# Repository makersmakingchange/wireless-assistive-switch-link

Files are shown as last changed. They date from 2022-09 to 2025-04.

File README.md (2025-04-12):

# Wireless Assistive Switch Link
The Wireless Assistive Switch Link is a device that enables a wireless connection between an assistive switch and an output device that has a 3.5 mm jack. In addition to momentary control, the device also has the option of pre-set timed latches of 10 seconds, 1 minute, or 5 minutes. This device may be useful for someone who would benefit from a wireless connection between the switch and the output device or using the latching feature for output devices. 

## Usage
An assistive switch is connected to the 3.5 mm jack on the transmitter. The 3.5 mm plug on the receiver is then connected to the input of the device to be controlled. With the receiver powered on, the receiver will activate the output device when the assistive switch is activated. 
The device can operate in several modes:

•	Momentary Switch: The output device will turn off about 0.5 seconds after the user stops pressing the switch.

•	Toggle Switch: Activating the assistive switch will activate the output device. The output device will remain on until the assistive switch is released, and pressed again. 

•	10 Second Latched Timer: After the assistive switch is pressed and released, the output device will remain on for 10 seconds and then turn off.

•	1 Minute Latched Timer: After the assistive switch is pressed and released, the output device will remain on for 1 minute and then turn off.

•	5 Minute Latched Timer: After the assistive switch is pressed and released, the output device will remain on for 5 minutes and then turn off. 

The mode can be changed by pressing the Mode Button on the Receiver. See the User Guide for instructions.

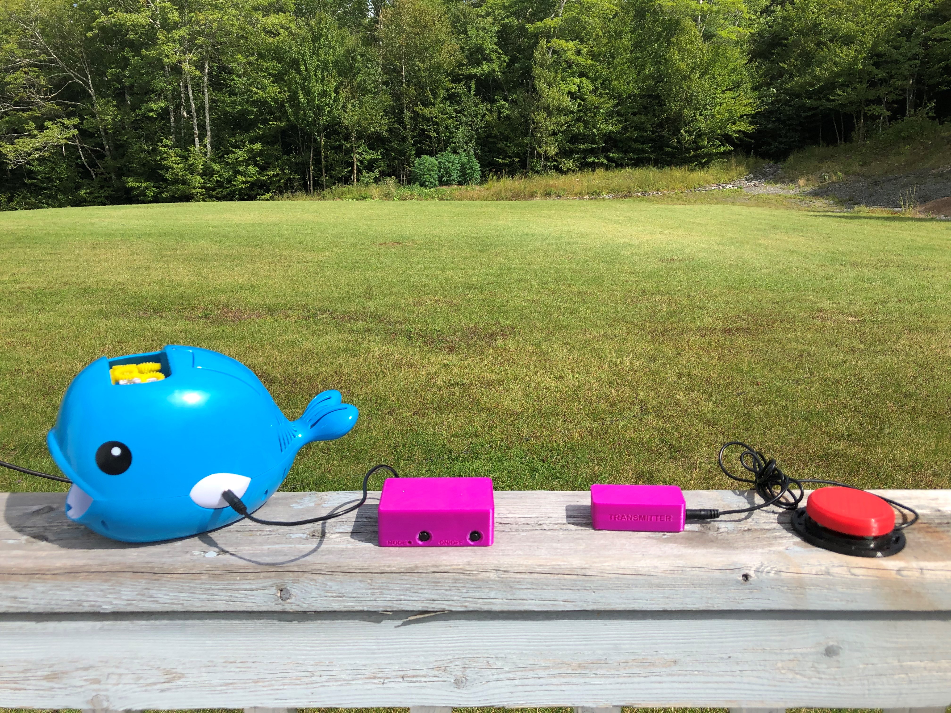
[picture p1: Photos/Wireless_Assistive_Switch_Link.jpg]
A picture of a 3d printed Wireless Assistive Switch Link. An Interact Switch is attached to the transmitter and a switch adapted whale toy is attached to the receiver.


## More info at
- [Makers Making Change Project Page](https://makersmakingchange.com/project/wireless-assistive-switch-link/)

## How to Obtain a Wireless Assistive Switch Link

### 1. Do it Yourself (DIY) or Do it Together (DIT)

This is an open-source assistive technology, so anyone is free to build it. All of the files and instructions required to build the device are contained within this repository. Refer to the Maker Checklist below.

### 2. Request a build of this device

If you would like to obtain this device, you may submit a build request through the [MMC Library Page](https://makersmakingchange.com/project/wireless-assistive-switch-link/). The requestor is responsible for the cost of materials and any shipping.

### 3. How to build this device for someone else

If you have the skills and equipment to build this device, and would like to donate your time to create the switch for someone who needs it, visit the [MMC Maker Wanted](https://makersmakingchange.com/maker-wanted/) section.

## Getting Started

### 1. Read the Makers Checklist

The Makers Checklist provides an overview of the steps required to build this device.

### 2. Order the Off-The-Shelf Components

The [Bill of Materials](/Documentation/Wireless_Assistive_Switch_Link_BOM_v1.0.xlsx) lists all of the parts and components required to build the Open Wobble Switch. The main switch component needs to be ordered online. The rest of the off-the-shelf components are also online or may be available in smaller quantities at your local hardware store or dollar store.

### 3. Print the 3D Printable components

All of the files and individual print files can be in the [/Build_Files/3D_Printing_Files](/Build_Files/3D_Printing/) folder.

### 4. Assemble the Device

Reference the [Assembly Guide](/Documentation/Wireless_Assistive_Switch_Link_Assembly_Guide_v1.0.pdf) for the tools and steps required to build each portion.

## Files
### Documentation
| Document             | Version | Link |
|----------------------|---------|------|
| Design Rationale     | 1.0     | [Wireless Assistive Switch Link_Design_Rationale](/Documentation/Wireless_Assistive_Switch_Link_Design_Rationale_v1.0.pdf)     |
| Maker Checklist      | 1.0     | [Wireless Assistive Switch Link_Maker_Checklist](/Documentation/Wireless_Assistive_Switch_Link_Maker_Checklist_v1.0.pdf)     |
| Bill of Materials    | 1.0     | [Wireless Assistive Switch Link_Bill_of_Materials](/Documentation/Wireless_Assistive_Switch_Link_BOM_v1.0.xlsx)     |
| 3D Printing Guide    | 1.0     | [Wireless Assistive Switch Link_3D_Printing_Guide](/Documentation/Wireless_Assistive_Switch_Link_3D_Printing_Guide_v1.0.pdf)     |
| Assembly Guide       | 1.0     | [Wireless Assistive Switch Link_Assembly_Guide](/Documentation/Wireless_Assistive_Switch_Link_Assembly_Guide_v1.0.pdf)     |
| User Guide           | 1.0     | [Wireless Assistive Switch Link_User_Guide](/Documentation/Wireless_Assistive_Switch_Link_User_Guide_v1.0.pdf)    |
| Changelog            | 1.0     | [Wireless Assistive Switch Link_Changelog](/Documentation/Wireless_Assistive_Switch_Link_Changelog_v1.0.pdf)     |

### Design Files
 - [CAD Files](/Design_Files)

### Build Files
 - [3D Printing Files](/Build_Files/3D_Printing_Files)

## Attribution
Designers:
 - Kerilyn Kennedy, Makers Making Change

## License
Everything needed or used to design, make, test, or prepare the Wireless Assistive Switch Link is licensed under the CERN 2.0 Permissive license <https://ohwr.org/project/cernohl/wikis/Documents/CERN-OHL-version-2> (CERN-OHL-P) . 

Accompanying material such as instruction manuals, videos, and other copyrightable works that are useful but not necessary to design, make, test, or prepare the Wireless Assistive Switch Link are published under a Creative Commons Attribution-ShareAlike 4.0 license https://creativecommons.org/licenses/by-sa/4.0/ (CC BY-SA 4.0).

----
<!-- ABOUT MMC START -->
## About Makers Making Change
[Makers Making Change Logo](https://www.makersmakingchange.com/)

Makers Making Change is a program of [Neil Squire](https://www.neilsquire.ca/), a Canadian non-profit that uses technology, knowledge, and passion to empower people with disabilities.

Makers Making Change leverages the capacity of community based Makers, Disability Professionals and Volunteers to develop and deliver affordable Open Source Assistive Technologies.

 - Website: [www.MakersMakingChange.com](https://www.makersmakingchange.com/)
 - GitHub: [makersmakingchange](https://github.com/makersmakingchange)
 - Bluesky: [@makersmakingchange.bsky.social](https://bsky.app/profile/makersmakingchange.bsky.social)
 - Instagram: [@makersmakingchange](https://www.instagram.com/makersmakingchange)
 - Facebook: [makersmakechange](https://www.facebook.com/makersmakechange)
 - LinkedIn: [Neil Squire Society](https://www.linkedin.com/company/neil-squire-society/)
 - Thingiverse: [makersmakingchange](https://www.thingiverse.com/makersmakingchange/about)
 - Printables: [MakersMakingChange](https://www.printables.com/@MakersMakingChange)

### Contact Us
For technical questions, to get involved, or to share your experience we encourage you to [visit our website](https://www.makersmakingchange.com/) or [contact us](https://www.makersmakingchange.com/s/contact).
<!-- ABOUT MMC END -->

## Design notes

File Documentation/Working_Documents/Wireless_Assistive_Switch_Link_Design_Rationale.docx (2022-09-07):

# Introduction

The purpose of this project was to create a cost-effective, maker-manufacturable wireless connection between an assistive switch and a device that has a 3.5 mm jack. This may be useful for someone who would benefit from or would prefer not to use a wired switch and is looking to connect to a device with an existing 3.5 mm switch input. For example, a suitable device may include a switch adapted toy.

# Research

There are a few existing commercial options, however they are quite expensive.

### Commercial wireless switches:

Name | Picture | Price | Link

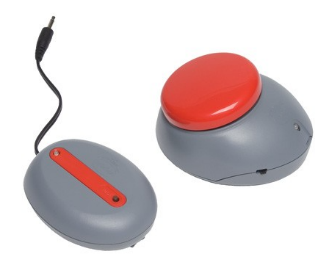
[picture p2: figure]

Jelly Beamer Twist Transmitter with Original Receiver | | $265 | Jelly Beamer Twist Transmitter with Original Receiver | eSpecial Needs (https://www.especialneeds.com/shop/assistive-technology/switches/wireless-switches/jelly-beamer-twist-transmitter-with-original-receiver.html)

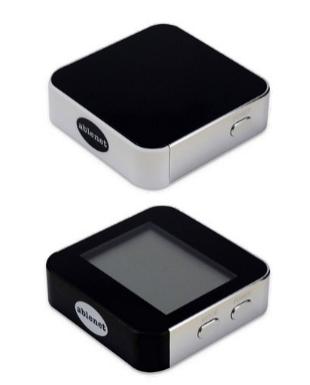
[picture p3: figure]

Mini Beamer Transmitter & Receiver Combo | | $265 | Mini Beamer Transmitter & Receiver Combo | Wireless Switches | eSpecial Needs (https://www.especialneeds.com/shop/assistive-technology/switches/wireless-switches/mini-beamer-transmitter-receiver-combo.html)

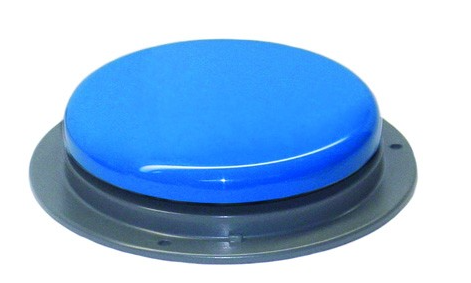
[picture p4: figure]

Big Beamer Transmitter | | $145 | Big Beamer Transmitter | Wireless Switches | Assistive Technology | eSpecial Needs (https://www.especialneeds.com/shop/assistive-technology/switches/wireless-switches/big-beamer-transmitter.html)

# Requirements

## Goals

G01 | Build a device that you can connect a 3.5 mm switch to and then have a wireless connection to a device that uses a 3.5 mm input jack.
G02 | Minimal delay between activation of the assistive switch and activation of the switch-adapted device.

## Functional Requirements

F01 | The device shall enable an assistive switch to operate a switch-adapted device through a wireless connection from a receiver to a transmitter.
F02 | The transmitter shall have an input for a 3.5 mm audio jack.
F03 | The receiver shall have an output for a 3.5 mm audio jack.
F04 | The device shall have sufficient range to operate across a room (i.e., 10 m range).

## Non-functional Requirement

NF01 | Uses easy to source parts.
NF02 | Maker friendly.

## Constraints

C01 | Costs significantly less than other commercial options.

# Ideation

The initial idea for the project was based on a similar project that used Zigbee communication protocol. Unfortunately, the cost of materials for that project was comparable to commercially available wireless switch links, so a less expensive approach was desired. After looking at a variety of wireless communication modules, an inexpensive commercially available remote-control receiver and transmitter was found.

# Conceptual Design

The primary concept was to investigate whether a commercially available wireless remote relay could be modified to include a 3.5 mm input on the transmitter / remote side and a 3.5 mm output on the receiver / relay side.

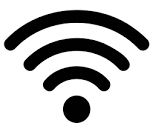
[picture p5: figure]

Output

Device

Transmitter

Receiver

Assistive

Switch

# Prototyping

An initial prototype was built to as a proof-of-concept.

A Wireless Relay Remote Control Switch 1 Channel Key Receiver + Transmitter was selected as it was an affordable option (~$20 CAD) that should be easy for makers to modify. The remote transmitter was switch adapted with a 3.5 mm switch jack and a 3.5 mm output connection was connected between the common and normally open pins.

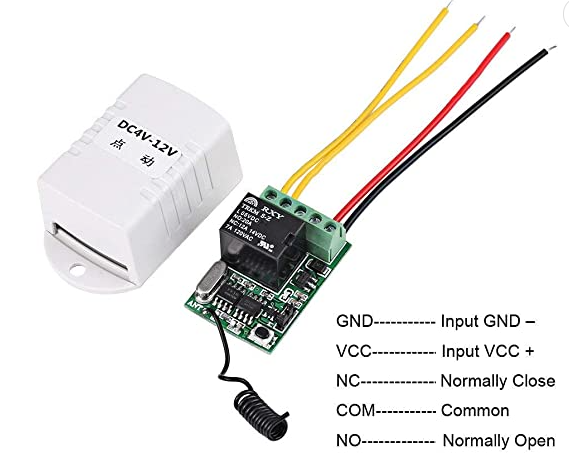
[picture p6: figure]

Figure 1: Device Wiring Diagram.[^1]

The prototype was tested using a DIY assistive switch and a switch-adapted toy. Testing confirmed the basic operation of the device and a range of approximately 10 meters.

# Detailed Design

The device consists of a modified transmitter and a modified receiver, each contained within a 3d printed enclosure. These covers are intended to be taken off when the batteries in the devices need to be replaced.

## Transmitter

### Transmitter Wiring

The 3.5 mm input jack needs to be connected in parallel with the existing button on the remote. While the existing button could be removed, it was decided to solder to the connections so that either the assistive switch or the original button could be used for activation. Leaving the existing button provides a way to test the device in case an assistive switch isn’t available or isn’t working.

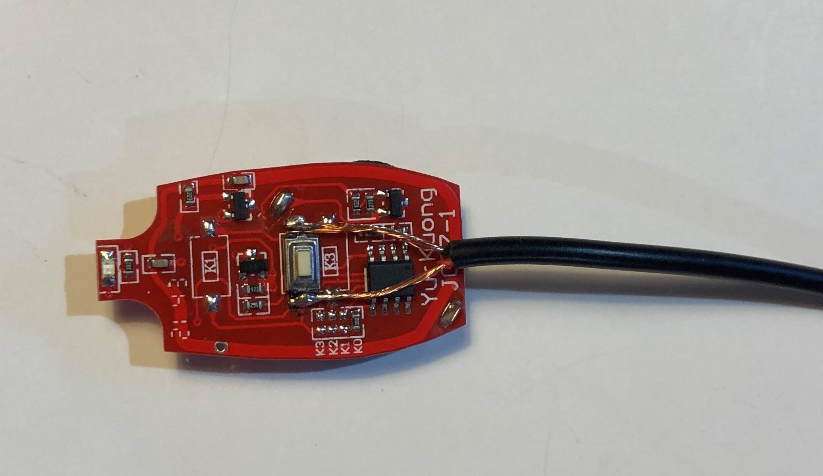
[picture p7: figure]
a picture of the wire soldered to the switch of the transmitter

Figure 2: Modified Transmitter with Assistive Switch soldered in parallel.

### Transmitter Enclosure

The original enclosure for the remote was not large enough to accommodate the 3.5 mm input connection, so a 3D printed enclosure was designed. It was decided to design the enclosures with a snap on fit cover to reduce the materials required to build the device, as well as to provide access to change batteries when needed. The enclosure was originally designed for a 3.5 mm panel mount jack, however to reduce material costs, a male-female extension cable was used instead and cut to provide both the female portion for the transmitter and the male portion for the receiver. However, the cable holes in the transmitter and receiver enclosures are designed to be large enough to be used with 3.5 mm jacks instead if it was preferred.

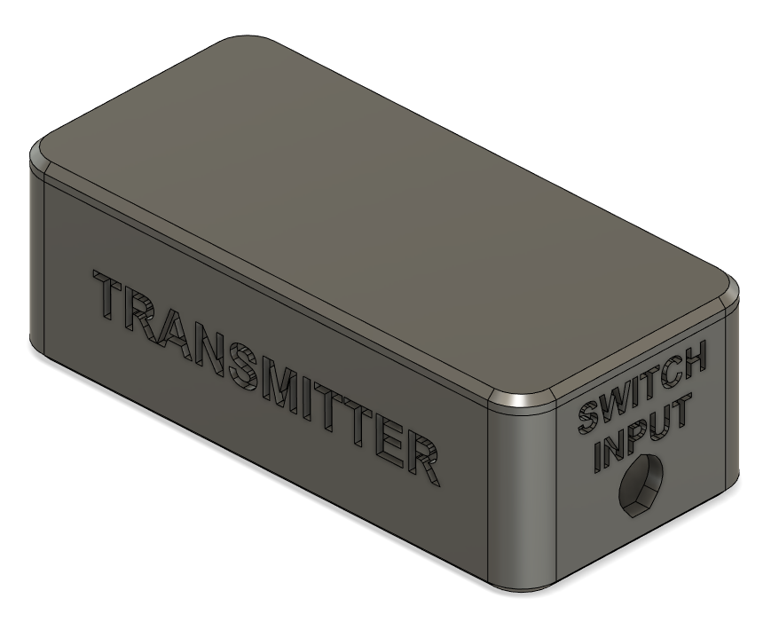
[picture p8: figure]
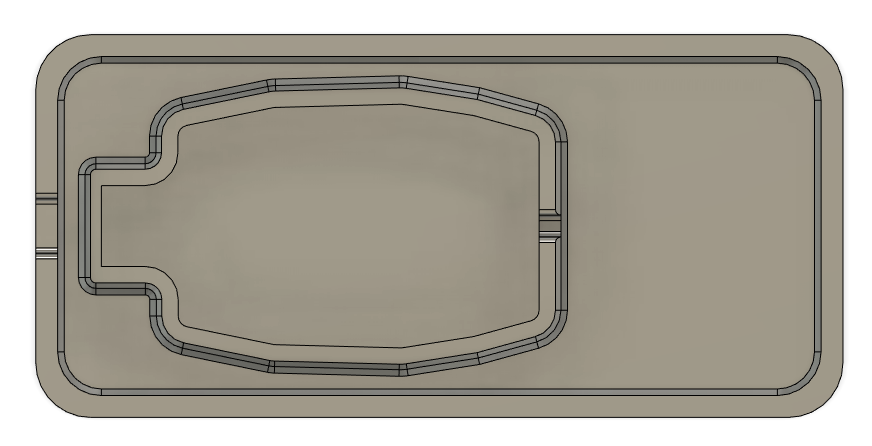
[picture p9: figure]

Figure 3: Wireless Assistive Switch Link Transmitter | Figure 4: Top view of the Transmitter's base

## Receiver

### Receiver Wiring

The Receiver requires a power source and a means to connect to the 3.5 mm device. Three AA batteries and a suitable holder were selected to provide 4.5 V.

A latching on/off switch was added to the circuit of the receiver because the receiver was always searching for the signal from the transmitter. Without the switch, it was found the battery life for the 3 AA batteries was only approximately 3 weeks long. The latching switch used for the on/off of the batteries in the receiver came in a pack of 10, so a second switch was used for the “mode” button on the device. The original mode button on the receiver was quite small and it was determined to be easier to add a switch in parallel rather than adding 3d components to press down on the existing button. The original mode button was not a latching switch, but since the latching one came in the pack of 10 it was decided to make a latching one work instead to eliminate the need for purchasing a momentary switch. The wires that originally came on the remote device and the battery holder were repurposed to avoid the need to purchase any additional wire.

### Receiver Enclosure

The Receiver Enclosure requires space to house the original receiver circuitry, the battery holder, and the buttons for controlling the power and changing the mode. A snap fit cover was included for this enclosure as well to provide easy, tool-free access to change the receiver batteries.

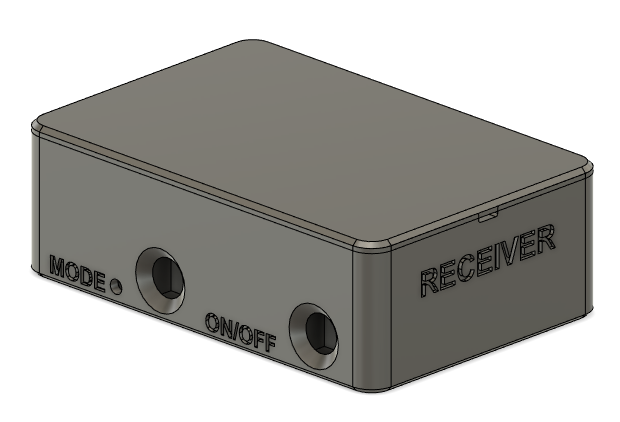
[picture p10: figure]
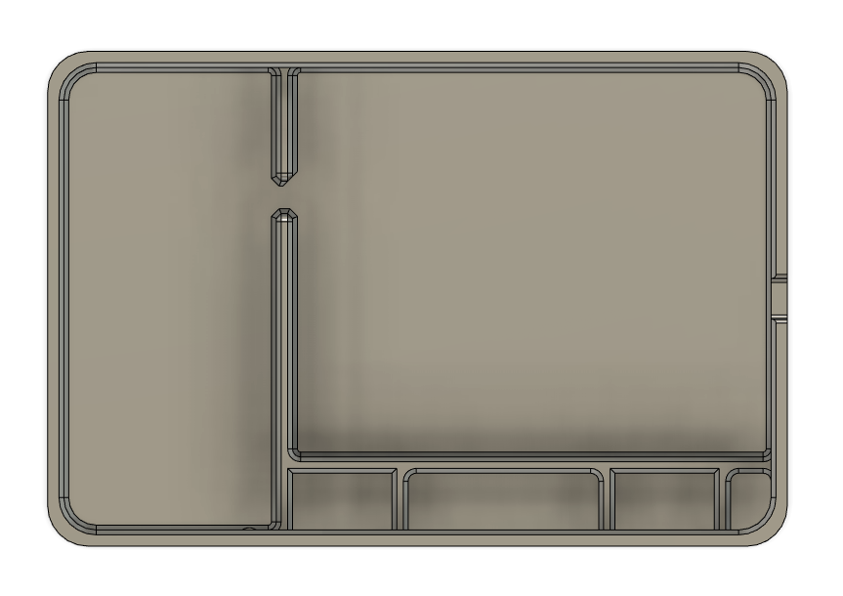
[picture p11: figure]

Figure 5: Wireless Assistive Switch Link Receiver | Figure 6: Top view of the Receiver's base

## Final Design

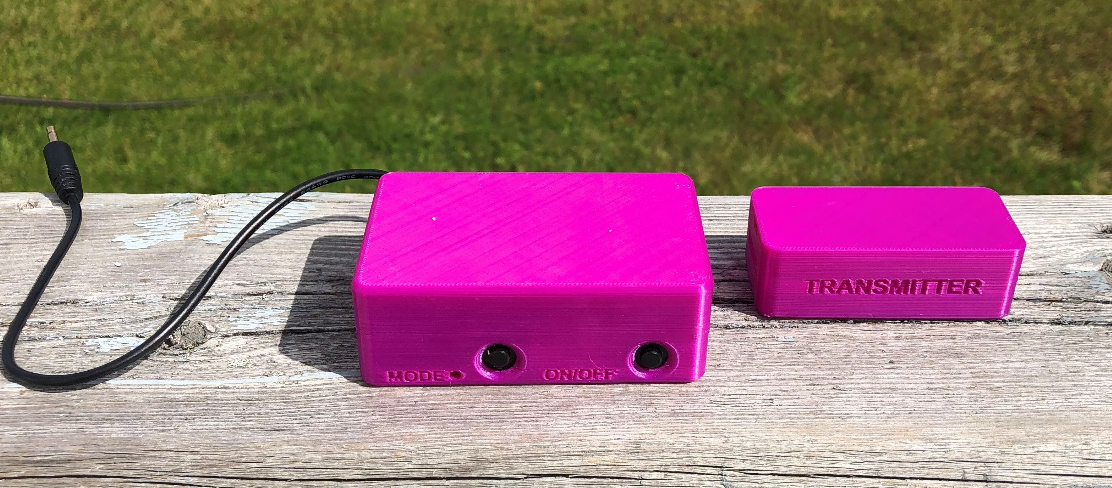
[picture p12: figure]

# Testing

As well as ensure that if a user owned 2 of these devices, that they would not interfere with one another.

# Opportunities for Improvement

- Adding an LED to indicate whether the receiver is on or off
- Making the mode light more visible. It cannot be seen if the surroundings are too bright (it is very challenging to see when outside).
- Finding a device that may have less of a delay. This device currently is likely not suitable for output devices that require negligible delay such as gaming.

[^1] Source: https://m.media-amazon.com/images/I/61aabXVLcAL._AC_SL1001_.jpg

© 2022 by Neil Squire / Makers Making Change. This work is licensed under the CC BY SA 4.0 License: http://creativecommons.org/licenses/by-sa/4.0 Files available at https://makersmakingchange.com/project/wireless-assistive-switch-link/ Page 3 of 3

V1.0 | AUGUST 2022 Wireless Assistive Switch Link Design Rationale

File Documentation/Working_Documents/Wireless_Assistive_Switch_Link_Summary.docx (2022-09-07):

# Title

Wireless Assistive Switch Link

## Subtitle

Provides a wireless link between a 3.5 mm switch and an output device that has a 3.5 mm jack.

## Device Specifications

Build Time:

< 1hr

1-4 hr

5-10hr

>10hr

Cost:

$0 - $10

$11 - $25

$26 - $50

$51 - $100

$101 - $250

$250+

Stage: Recently Added

Skills: Soldering, 3D Printing, Mechanics

Need: Mobility, Agility, Dexterity

Disability: Mobility / Physical

Difficulty: Intermediate

License: Attribution-ShareAlike 4.0 International

Usages: Aids for Daily Living, Mobility, Recreation and Leisure

Type: Switch Interfaces, Adapted Toys

## Device Details

### Overview

The Wireless Assistive Switch Link is a device that enables a wireless connection between an assistive switch and an output device that has a 3.5 mm jack. In addition to momentary control, the device also has the option of pre-set timed latches of 10 seconds, 1 minute, or 5 minutes. This device may be useful for someone who would benefit from a wireless connection between the switch and the output device or using the latching feature for output devices.

### Usage

An assistive switch is connected to the 3.5 mm jack on the transmitter. The 3.5 mm plug on the receiver is then connected to the input of the device to be controlled. With the receiver powered on, the receiver will activate the output device when the assistive switch is activated.

The device can operate in several modes:

- Momentary Switch: The output device will turn off about 0.5 seconds after the user stops pressing the switch.
- Toggle Switch: Activating the assistive switch will activate the output device. The output device will remain on until the assistive switch is released, and pressed again.
- 10 Second Latched Timer: After the assistive switch is pressed and released, the output device will remain on for 10 seconds and then turn off.
- 1 Minute Latched Timer: After the assistive switch is pressed and released, the output device will remain on for 1 minute and then turn off.
- 5 Minute Latched Timer: After the assistive switch is pressed and released, the output device will remain on for 5 minutes and then turn off.

The mode can be changed by pressing the Mode Button on the Receiver. See the User Guide for instructions.

### Cost

This device can be built for approximately $40.

### Build Instructions

This build consists of 3D printable parts and some commercial off-the-shelf hardware. Refer to the Assembly Guide, Bill of Materials, and 3D Print Guide for instructions on what parts to obtain, and how to print the parts.

#### Skills Required

- Soldering
- 3D Printing
- Mechanics

#### Time Required

3D Printing Time: 5 hours 30 minutes

Assembly Time: < 1 hour

#### Tools

- Small Phillips screwdriver
- Soldering Iron and Solder
- Wire Strippers

#### Components

- Wireless Relay Remote
- Battery holder for 3 AA batteries
- 3 x AA batteries
- 2x Latching Switches
- 1x 3.5mm Male to Female Cable

#### 3D Printing

Refer to the Maker Guide for 3D Printing Instructions.

### Design

This device was designed in Autodesk Fusion 360. Original design files are in the repository.

### Attribution

Designed by Kerilyn Kennedy – Makers Making Change

Documentation by Neil Squire / Makers Making Change

© 2022 by Neil Squire / Makers Making Change. This work is licensed under the CC BY SA 4.0 License: http://creativecommons.org/licenses/by-sa/4.0 Files available at https://makersmakingchange.com/project/wireless-assistive-switch-link/ Page 1 of 2

V1.0 | AUGUST 2022 Wireless Assistive Switch Link Summary

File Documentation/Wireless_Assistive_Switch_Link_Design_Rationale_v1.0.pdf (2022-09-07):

V1.0 | AUGUST 2022

## Wireless Assistive Switch Link

## DESIGN RATIONALE

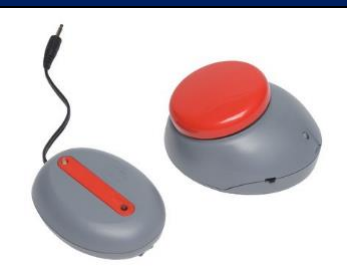
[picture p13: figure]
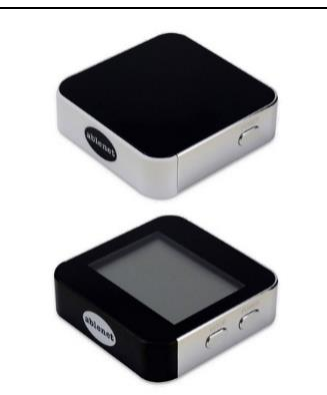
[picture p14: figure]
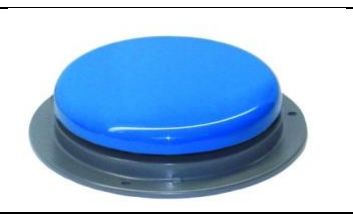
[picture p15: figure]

© 2022 by Neil Squire / Makers Making Change. This work is licensed under the CC BY SA 4.0 License: http://creativecommons.org/licenses/by-sa/4.0
Files available at https://makersmakingchange.com/project/wireless-assistive-switch-link/ | Page 1 of 7

### Introduction

The purpose of this project was to create a cost-effective, maker-manufacturable wireless connection between an assistive switch and a device that has a 3.5 mm jack. This may be useful for someone who would benefit from or would prefer not to use a wired switch and is looking to connect to a device with an existing 3.5 mm switch input. For example, a suitable device may include a switch adapted toy.

### Research

There are a few existing commercial options, however they are quite expensive.

Commercial wireless switches:
Name | Picture | Price | Link
Jelly Beamer Twist Transmitter with Original Receiver | | $265 | Jelly Beamer Twist Transmitter with Original Receiver | eSpecial Needs (https://www.especialneeds.com/shop/assistive-technology/switches/wireless-switches/jelly-beamer-twist-transmitter-with-original-receiver.html)
Mini Beamer Transmitter & Receiver Combo | | $265 | Mini Beamer Transmitter & Receiver Combo | Wireless Switches | eSpecial Needs (https://www.especialneeds.com/shop/assistive-technology/switches/wireless-switches/mini-beamer-transmitter-receiver-combo.html)
Big Beamer Transmitter | | $145 | Big Beamer Transmitter | Wireless Switches | Assistive Technology | eSpecial Needs (https://www.especialneeds.com/shop/assistive-technology/switches/wireless-switches/big-beamer-transmitter.html)

## DESIGN RATIONALE

Files available at https://makersmakingchange.com/project/wireless-assistive-switch-link/ | Page 2 of 7

### Requirements

### Goals

G01 | Build a device that you can connect a 3.5 mm switch to and then have a wireless connection to a device that uses a 3.5 mm input jack.
G02 | Minimal delay between activation of the assistive switch and activation of the switch-adapted device.

### Functional Requirements

F01 | The device shall enable an assistive switch to operate a switch-adapted device through a wireless connection from a receiver to a transmitter.
F02 | The transmitter shall have an input for a 3.5 mm audio jack.
F03 | The receiver shall have an output for a 3.5 mm audio jack.
F04 | The device shall have sufficient range to operate across a room (i.e., 10 m range).

### Non-functional Requirement

NF01 | Uses easy to source parts.
NF02 | Maker friendly.

### Constraints

C01 Costs significantly less than other commercial options.

## DESIGN RATIONALE

Files available at https://makersmakingchange.com/project/wireless-assistive-switch-link/ | Page 3 of 7

### Ideation

The initial idea for the project was based on a similar project that used Zigbee communication protocol. Unfortunately, the cost of materials for that project was comparable to commercially available wireless switch links, so a less expensive approach was desired. After looking at a variety of wireless communication modules, an inexpensive commercially available remote-control receiver and transmitter was found.

### Conceptual Design

The primary concept was to investigate whether a commercially available wireless remote relay could be modified to include a 3.5 mm input on the transmitter / remote side and a 3.5 mm output on the receiver / relay side.

### Prototyping

An initial prototype was built to as a proof-of-concept.

A Wireless Relay Remote Control Switch 1 Channel Key Receiver + Transmitter was selected as it was an affordable option (~$20 CAD) that should be easy for makers to modify. The remote transmitter was switch adapted with a 3.5 mm switch jack and a 3.5 mm output connection was connected between the common and normally open pins.

Assistive

Switch

Transmitter | Receiver

Output

Device

## DESIGN RATIONALE

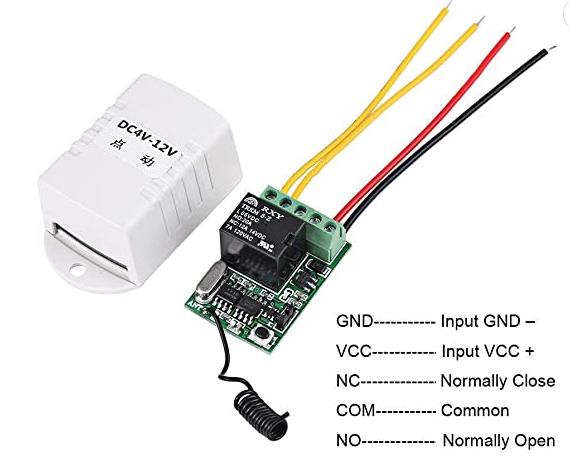
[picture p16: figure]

Files available at https://makersmakingchange.com/project/wireless-assistive-switch-link/ | Page 4 of 7

Figure 1: Device Wiring Diagram.¹

The prototype was tested using a DIY assistive switch and a switch-adapted toy. Testing confirmed the basic operation of the device and a range of approximately 10 meters.

### Detailed Design

The device consists of a modified transmitter and a modified receiver, each contained within a 3d printed enclosure. These covers are intended to be taken off when the batteries in the devices need to be replaced.

### Transmitter

Transmitter Wiring
The 3.5 mm input jack needs to be connected in parallel with the existing button on the remote. While the existing button could be removed, it was decided to solder to the connections so that either the assistive switch or the original button could be used for activation. Leaving the existing button provides a way to test the device in case an assistive switch isn’t available or isn’t working.

1
Source: https://m.media-amazon.com/images/I/61aabXVLcAL._AC_SL1001_.jpg

## DESIGN RATIONALE

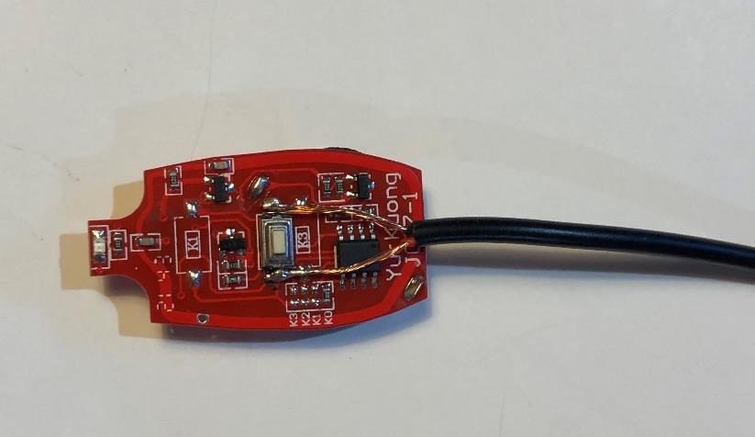
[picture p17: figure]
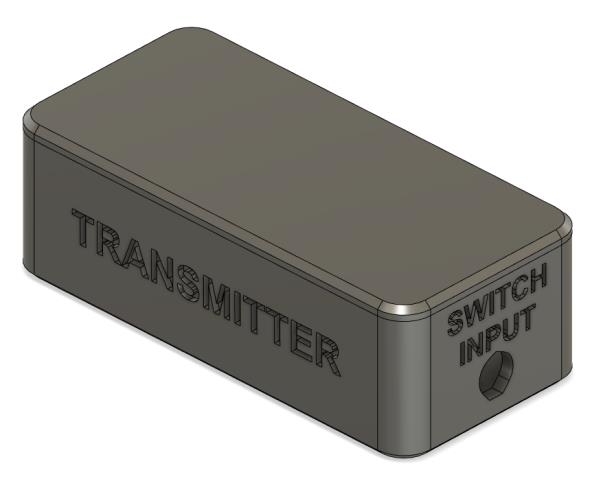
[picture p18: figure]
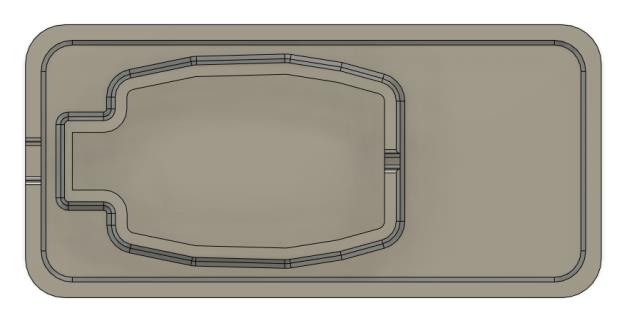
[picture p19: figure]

Files available at https://makersmakingchange.com/project/wireless-assistive-switch-link/ | Page 5 of 7

Figure 2: Modified Transmitter with Assistive Switch soldered in parallel.

Transmitter Enclosure
The original enclosure for the remote was not large enough to accommodate the 3.5 mm input connection, so a 3D printed enclosure was designed. It was decided to design the enclosures with a snap on fit cover to reduce the materials required to build the device, as well as to provide access to change batteries when needed. The enclosure was originally designed for a 3.5 mm panel mount jack, however to reduce material costs, a male-female extension cable was used instead and cut to provide both the female portion for the transmitter and the male portion for the receiver. However, the cable holes in the transmitter and receiver enclosures are designed to be large enough to be used with 3.5 mm jacks instead if it was preferred.
Figure 3: Wireless Assistive Switch Link Transmitter | Figure 4: Top view of the Transmitter's base

## DESIGN RATIONALE

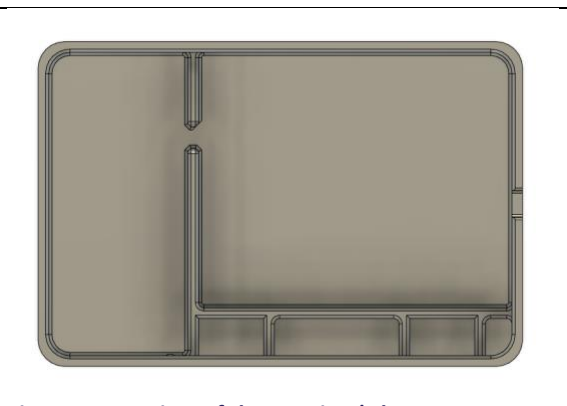
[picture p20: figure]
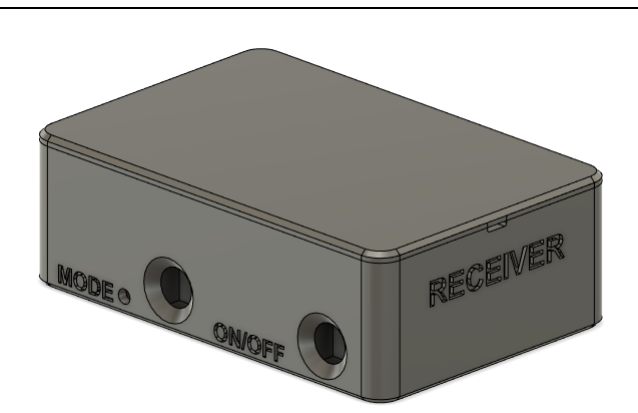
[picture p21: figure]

Files available at https://makersmakingchange.com/project/wireless-assistive-switch-link/ | Page 6 of 7

### Receiver

Receiver Wiring
The Receiver requires a power source and a means to connect to the 3.5 mm device. Three AA batteries and a suitable holder were selected to provide 4.5 V.

A latching on/off switch was added to the circuit of the receiver because the receiver was always searching for the signal from the transmitter. Without the switch, it was found the battery life for the 3 AA batteries was only approximately 3 weeks long. The latching switch used for the on/off of the batteries in the receiver came in a pack of 10, so a second switch was used for the “mode” button on the device. The original mode button on the receiver was quite small and it was determined to be easier to add a switch in parallel rather than adding 3d components to press down on the existing button. The original mode button was not a latching switch, but since the latching one came in the pack of 10 it was decided to make a latching one work instead to eliminate the need for purchasing a momentary switch. The wires that originally came on the remote device and the battery holder were repurposed to avoid the need to purchase any additional wire.

Receiver Enclosure
The Receiver Enclosure requires space to house the original receiver circuitry, the battery holder, and the buttons for controlling the power and changing the mode. A snap fit cover was included for this enclosure as well to provide easy, tool-free access to change the receiver batteries.
Figure 5: Wireless Assistive Switch Link Receiver | Figure 6: Top view of the Receiver's base

## DESIGN RATIONALE

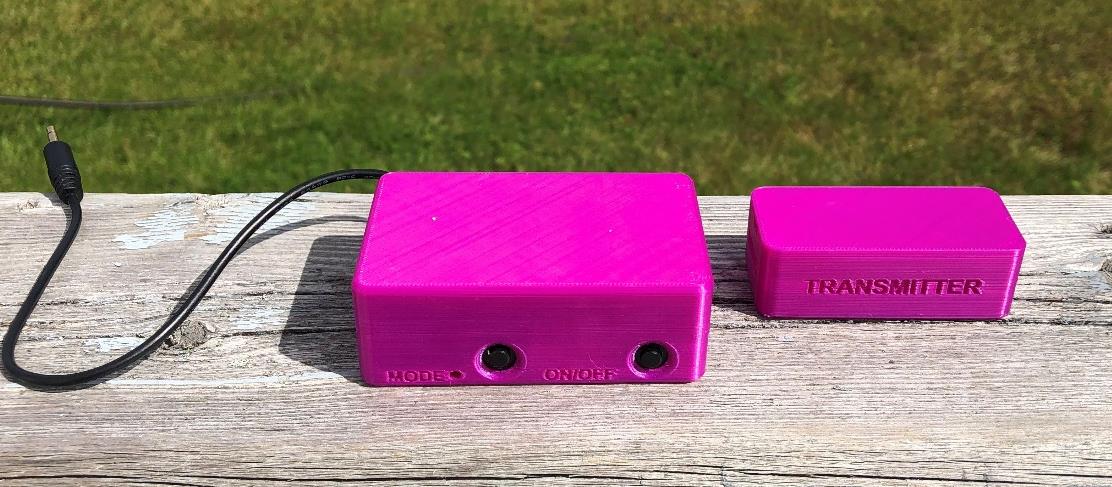
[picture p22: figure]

Files available at https://makersmakingchange.com/project/wireless-assistive-switch-link/ | Page 7 of 7

### Final Design

### Testing

As well as ensure that if a user owned 2 of these devices, that they would not interfere with one another.

### Opportunities for Improvement

- Adding an LED to indicate whether the receiver is on or off
- Making the mode light more visible. It cannot be seen if the surroundings are too bright (it is very challenging to see when outside).
- Finding a device that may have less of a delay. This device currently is likely not suitable for output devices that require negligible delay such as gaming.

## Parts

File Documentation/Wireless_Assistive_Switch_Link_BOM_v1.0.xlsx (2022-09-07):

Device: Wireless Assistive Switch Device |  | Total Cost | Total Print time (hr) | Total filament (g)
Version: V1.0 | Date Created: August 2022 | $33.52 | 5.65 | 85
Commercial Parts:
Part type (Electrical. Mechanical, Sanitization, ect) | Part Name | Quantity Needed | Pkg Quantity | Price per package | Price per Unit | Price for qty needed | Link
Wireless Relay Remote Control Switch | Walfront2fzi0cwpgx | 1 | 1 | $20.67 | $20.67 | $20.67 | DC 4V 5V 6V 7.4V 9V 12V Wireless Relay Remote Control Switch 1 Channel Key Receiver + Transmitter for Computer, Auto Door, Window, Garage Door : Amazon.ca: Tools & Home Improvement (https://www.amazon.ca/gp/product/B0762HH45G/ref=ppx_yo_dt_b_asin_title_o01_s00?ie=UTF8&psc=1)
3 AA battery holder | ‎De-Cable-22h-318 | 1 | 8 | $10.99 | $1.37 | $1.37 | https://www.amazon.ca/Battery-Holder-2PCS-RFAdapter-Leads/dp/B089VP5Z27
Male to Female 3.5mm cable | ‎35MM-MF-6F | 1 | 1 | $6.49 | $6.49 | $6.49 | axGear Audio Extension Cable Male to Female, 3.5MM Stereo, Aux Cord for TV, Computer, Speaker, Smartphone and More [1 Pack] - 6ft - Black : Amazon.ca: Electronics (https://www.amazon.ca/axGear-3-5MM-Female-Stereo-Extension/dp/B0711GV65F?rnid=12035759011&s=electronics)
Uxcell Latching Switches | a13112600ux0650 | 2 | 10 | 12.2 | $1.22 | $2.44 | https://www.amazon.ca/gp/product/B00HGAKKAC/ref=ppx_yo_dt_b_asin_title_o05_s00?ie=UTF8&psc=1
3D Printed Parts ESTIMATED PRICING USING 1KG ROLL COST: | $30.00
Part | Description | Quantity Needed | TOTAL Mass (g) | Estimated Price | Print Time (Min) | Link
Transmitter Base |  | 1 | 20 | $0.60 | 90
Transmitter Cover |  | 1 | 10 | $0.30 | 35
Receiver Base |  | 1 | 36 | $1.08 | 154
Receiver Cover |  | 1 | 19 | $0.57 | 60
 |  |  |  | $0.00
 |  |  | Total Print Cost: | $2.55
Tools for Assembly
Small Phillips Screw Driver
Soldering Iron and Solder
Wire Strippers
Alternatives (if there are other sources for some parts link them below)
Part and description | Link
This adaption could also be done using 2 3.5mm jacks and a male:male 3.5mm cable
Male-Male 3.5mm cable: | AK-AV100 Assmann WSW Components | Cable Assemblies | DigiKey (https://www.digikey.ca/en/products/detail/assmann-wsw-components/AK-AV100/2181936)
3.5mm mono jacks: | https://www.digikey.ca/en/products/detail/schurter-inc/4832-2211/2646631

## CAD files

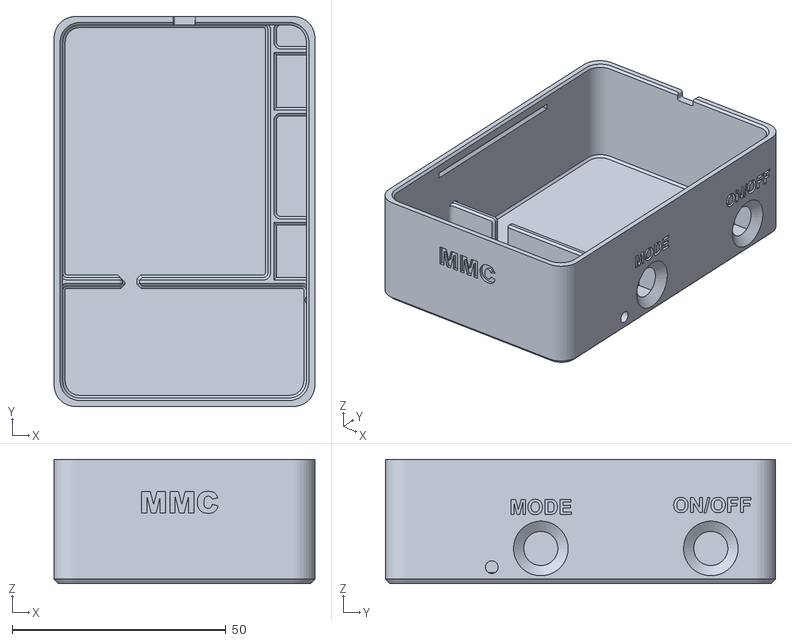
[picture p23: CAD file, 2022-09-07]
Build_Files/3D_Print_Files/Wireless_Receiver_Base.stl
61.0 x 91.2 x 29.0

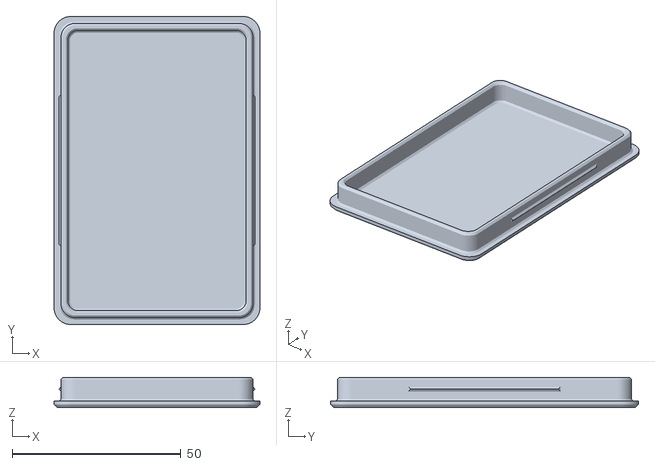
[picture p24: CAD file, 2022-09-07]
Build_Files/3D_Print_Files/Wireless_Receiver_Cover.stl
61.0 x 91.2 x 9.00

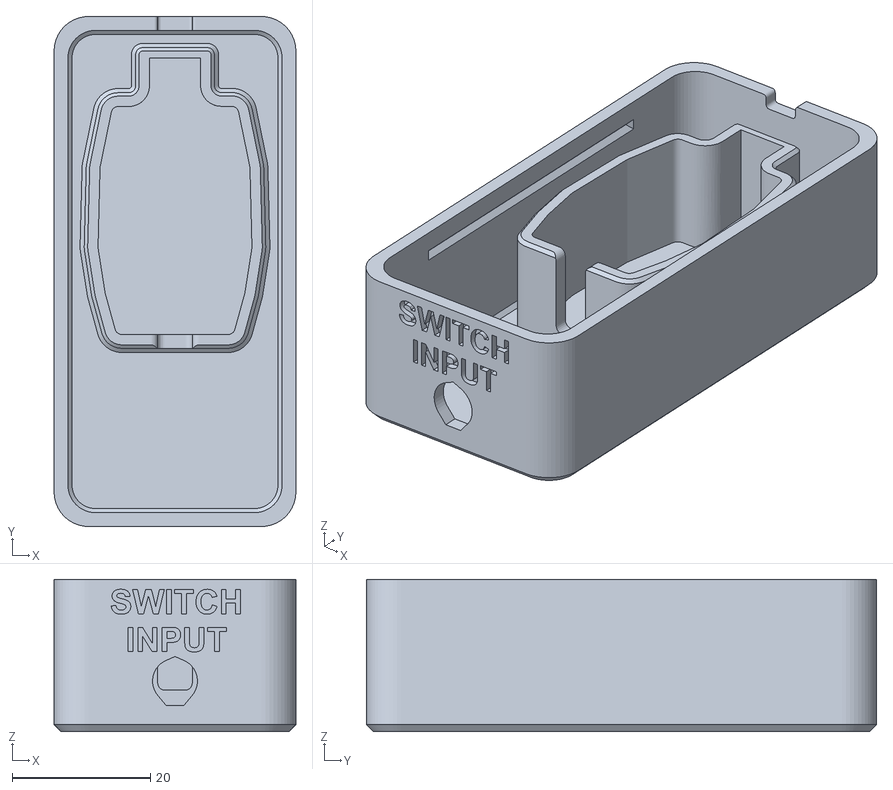
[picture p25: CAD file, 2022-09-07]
Build_Files/3D_Print_Files/Wireless_Transmitter_Base.stl
35.0 x 73.8 x 22.0

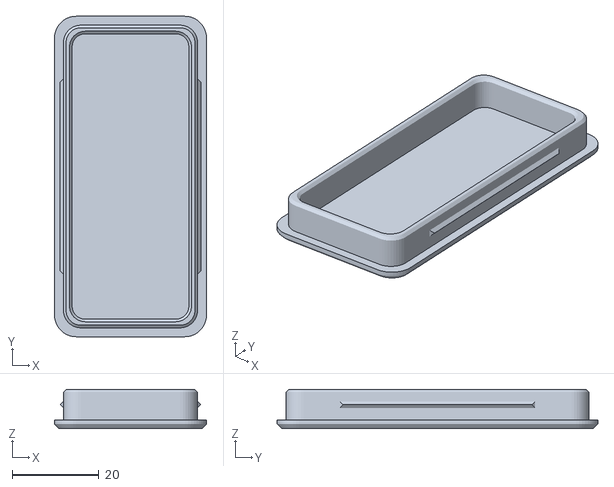
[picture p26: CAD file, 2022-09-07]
Build_Files/3D_Print_Files/Wireless_Transmitter_Cover.stl
35.0 x 73.8 x 9.00

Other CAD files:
Design_Files/Wireless_Receiver.f3d
Design_Files/Wireless_Transmitter.f3z

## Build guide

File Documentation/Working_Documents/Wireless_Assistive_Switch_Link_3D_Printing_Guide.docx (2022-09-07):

# 3D Printing Summary

Metrics | Wireless Assistive Switch Link
Total Print Time (min) | 339
Total Number of Components | 4
Typical Total Mass (g) | 85
Typical Number of Print Setups | 2

# 3D Printing Settings

Print File Name | Qty | Total Print Time (hr:min) | Mass (g) | Infill (%) | Support (Y/N) | Layer Height/ Nozzle Diameter (mm) | Notes (orientation, special settings, etc.)
Wireless_Transmitter_Cover.stl | 1 | 0:35 | 10 | 20 | N | 0.2/0.4 | Print in orientation given in STL
Wireless_Transmitter_Base.stl | 1 | 1:30 | 20 | 20 | N | 0.2/0.4 | Print in orientation given in STL
Wireless_Receiver_Cover.stl | 1 | 1:00 | 19 | 20 | N | 0.2/0.4 | Print in orientation given in STL
Wireless_Receiver_Base.stl | 1 | 2:34 | 36 | 20 | N | 0.2/0.4 | Print in orientation given in STL

# Customization Options

The user can request the colour of the devices or any custom markings they may want on them.

# Post-Processing

All parts are printed without supports, and no post-processing is required.

# Examples of Quality Prints

Below is a picture of what the quality of the print is expected to look like.

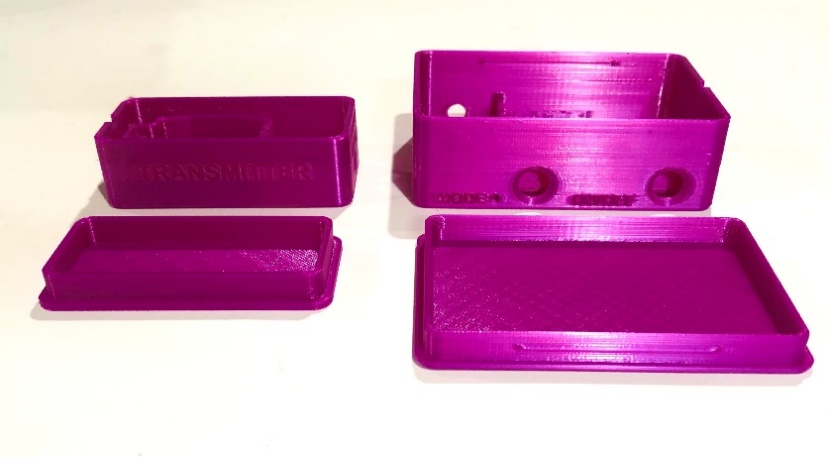
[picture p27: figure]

© 2022 by Neil Squire / Makers Making Change. This work is licensed under the CC BY SA 4.0 License: http://creativecommons.org/licenses/by-sa/4.0 Files available at https://makersmakingchange.com/project/wireless-assistive-switch-link/ Page 3 of 3

V1.0 | AUGUST 2022 Wireless Switch Assistive Switch 3D Printing Guide

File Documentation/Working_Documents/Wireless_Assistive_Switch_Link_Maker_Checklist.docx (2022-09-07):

# Maker To Do List

- Read through the Assembly Guide to become familiar with required components, tools, supplies, and safety gear and overall assembly steps
- Talk to User about customization options (e.g., color, any special requests, etc.)
- Order hardware components
- Gather tools, supplies, and safety equipment
- 3D Print the device enclosures
- Assemble the device
- Test device
- Print “User Quick Guide”

# Items to Give to User

- Assembled, tested device
- “User Quick Guide”

© 2022 by Neil Squire / Makers Making Change. This work is licensed under the CC BY SA 4.0 License: http://creativecommons.org/licenses/by-sa/4.0 Files available at https://makersmakingchange.com/project/wireless-assistive-switch-link/ Page 3 of 3

V1.0 | AUGUST 2022 Wireless Assistive Switch Link Maker Checklist

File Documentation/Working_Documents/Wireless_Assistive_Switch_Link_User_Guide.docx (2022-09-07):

## Introduction

The Wireless Assistive Switch Link is a device that enables a wireless connection between an assistive switch and an output device that has a 3.5 mm jack. The device also comes pre-set with timing latching settings of 10 seconds, 1 minute, and 5 minutes.

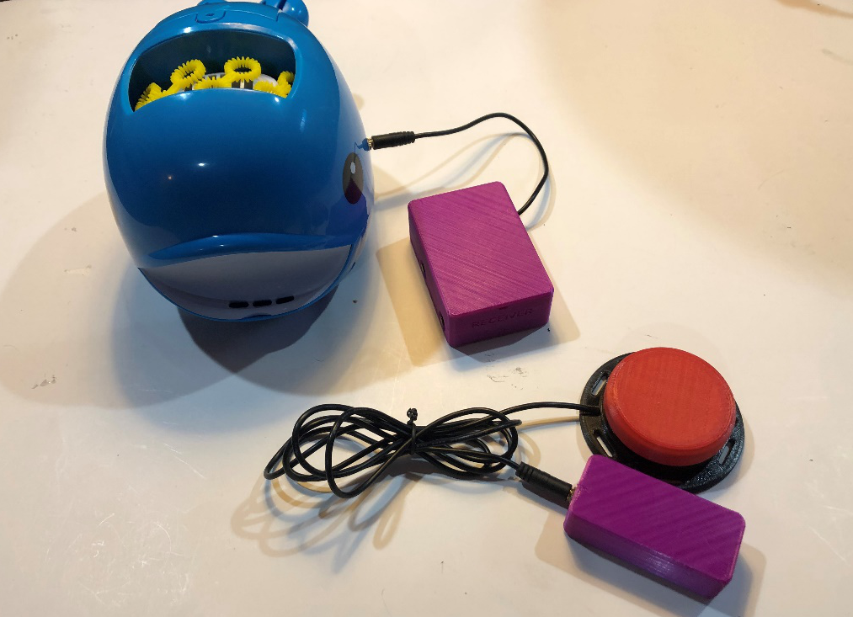
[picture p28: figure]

Assistive Switch

Transmitter

Receiver

Output Device

## Batteries

The Transmitter uses two CR2016 lithium batteries.

The Receiver uses three AA batteries.

## Compatibility

This device is compatible with any 3.5 mm assistive switch as well any output device that has a 3.5 mm input connection.

## Specifications

- Transmitter: 74mm Long x 35mm Wide x 22mm Deep
- Receiver: 91mm Long x 61mm Wide x 29mm Deep

## Cleaning

The outside of the Wireless Assistive Switch Link can be wiped down with a damp cloth. Please ensure that the inner contents of the device do not get wet.

## Usage

The Wireless Assistive Switch Link is used with a 3.5 mm switch, and an output device that has a 3.5 mm jack. The following is a set of instructions on how to use the device.

Step 1: Plug in an assistive switch into the device labelled “Transmitter”.

Step 2: Plug in an output device to the device labelled “Receiver”.

Step 3: Press the assistive switch. If nothing happens press the “On/Off” button on the side of the Receiver and try again.

Step 4: Determine what mode you want to use on the device. There are pre-set modes on the device, and some have been found to be more useful than others. They will be selected later by clicking the mode button again once you see the correct number of flashes as the desired mode. The following is a guide to explain the different modes:

- 1 flash = What seems to be an infinite latch? It does not appear to be useful and would recommend not using it.
- 2 flashes = momentary switch. The output device will turn off about 0.5 seconds after the user stops pressing the switch.
- 3 flashes = latching switch. It will stay on until you press the assistive switch again to turn it off.
- 4 flashes = switch latches for 10 seconds and then turns off.
- 5 flashes = switch latches for 1 minute and then turns off.
- 6 flashes = switch latches for 5 minutes and then turns off.
- 7 flashes = An “error”. Avoid using this setting. If you accidentally set the device to the 7th setting, it will not do anything. The device will have to be resynced by pressing the mode button twice quickly until the red light stays on. Next, click the assistive switch. Then, press the mode button again to pick the mode you want. The device should work again once this is complete.

Step 5: Once the desired mode has been determined, press the “Mode” button on the side of the receiver. It should do one flash, pause, two flashes, pause, 3 flashes, pause, all the way up to 7 flashes. To select a mode, press the mode button again after you see the number of flashes that corresponds with the mode you want. For example, if you are looking for the momentary switch mode (2 flashes), wait for the device to flash once, pause, and then flash twice before pressing the “Mode” button again.

Step 6: Press your assistive switch. The output device should act accordingly to the mode you selected.

Step 7: When you’re done using the device, turn the power off by pressing the “On/Off” button on the Receiver. This will save the battery life in the Receiver.

© 2022 by Neil Squire / Makers Making Change. This work is licensed under the CC BY SA 4.0 License: http://creativecommons.org/licenses/by-sa/4.0 Files available at https://makersmakingchange.com/project/wireless-assistive-switch-link/ Page 3 of 3

V1.0 | AUGUST 2022 Wireless Assistive Switch Link user Quick Guide

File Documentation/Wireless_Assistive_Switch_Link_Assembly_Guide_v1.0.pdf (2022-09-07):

V1.0 | AUGUST 2022

# Wireless Switch

# ASSEMBLY GUIDE

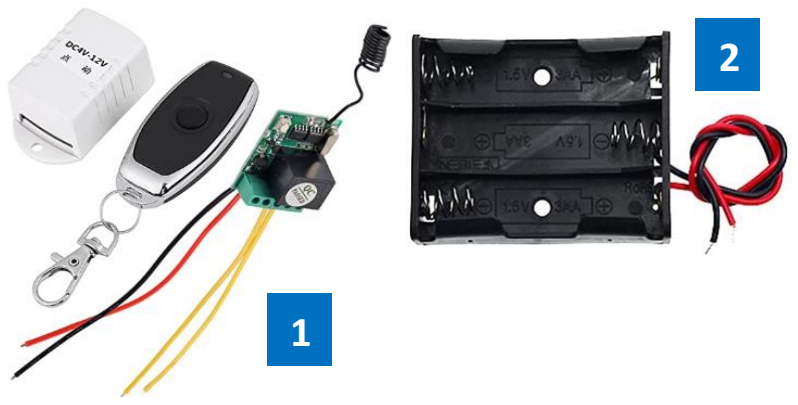
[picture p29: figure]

© 2022 by Neil Squire / Makers Making Change. This work is licensed under the CC BY SA 4.0 License: http://creativecommons.org/licenses/by-sa/4.0
Files available at https://makersmakingchange.com/project/wireless-assistive-switch-link/ | Page 1 of 18

# 1 Required Components

## BOM 1. Wireless Relay Remote

## Control Switch

## 2. Battery Holder for 3 AA

## batteries

## 3. 3x AA batteries

## 4. 2x Latching Switches

## 5. 3.5 mm Extension Cable

# 2 Required Tools

## - Small Phillips screwdriver - Soldering Iron and Solder - Wire strippers

# 3 Required Personal Protective Equipment (PPE)

## - Safety Glasses

3

4

5

# ASSEMBLY GUIDE

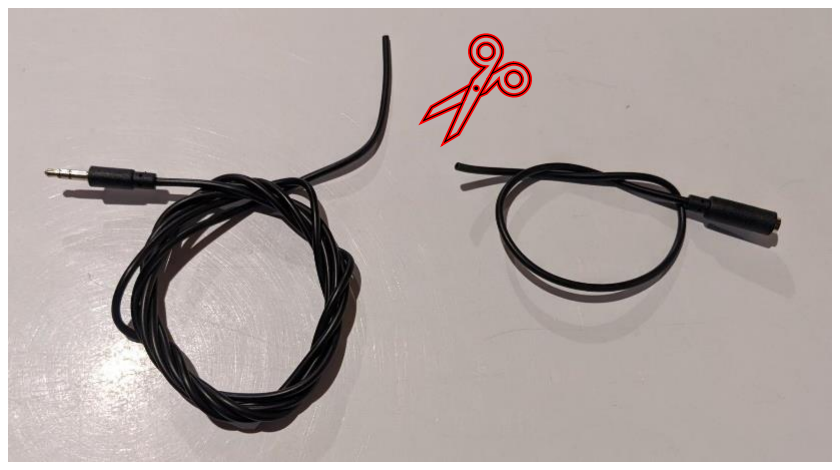
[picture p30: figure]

Files available at https://makersmakingchange.com/project/wireless-assistive-switch-link/ | Page 2 of 18

# 4 Assembly Instructions

## 4.1 Preparation

## 4.1.1 Cut Cable

With the 3.5 mm male to female cable, cut the cord so that the end with the jack (male end) is 60 cm (2 ft) long and the end with the plug (female end) is 30 cm (1 ft) long. If your cable is longer than 90 cm (3 ft), you can discard the remainder of the cable.

## 4.1.2 Strip Cable Ends

Once the cable is cut, strip both the cut ends of the female and male wires about 2 cm. If there are still two wires enclosed in plastic, the individual wires will also have to be stripped approximately 0.5 cm. Twist the wires so that they don’t get mixed up.

# ASSEMBLY GUIDE

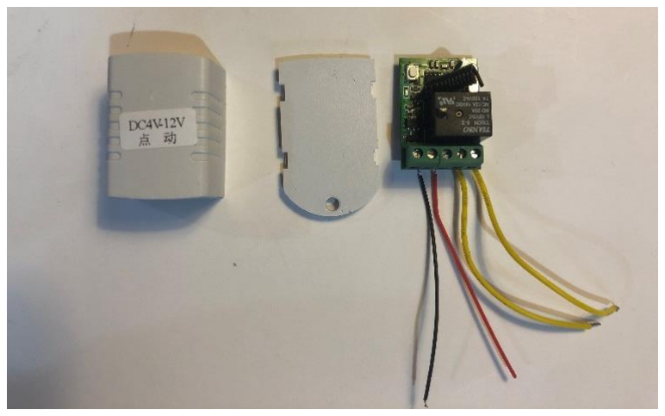
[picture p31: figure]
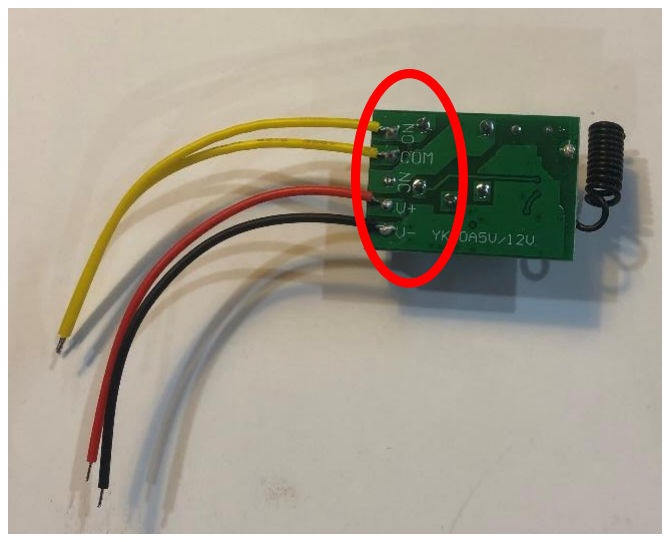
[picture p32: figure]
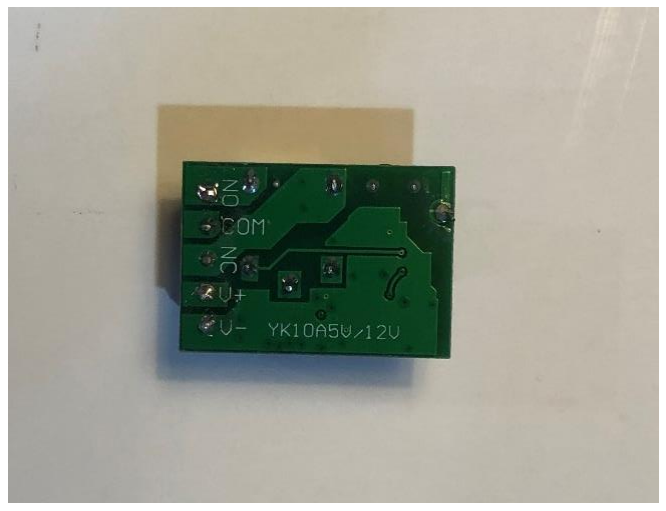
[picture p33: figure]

Files available at https://makersmakingchange.com/project/wireless-assistive-switch-link/ | Page 3 of 18

## 4.2 Receiver

## 4.2.1 Remove Enclosure

Open and set aside the case around the receiver.

## 4.2.2 Desolder wires

Desolder all 4 wires from the bottom of the receiver. Set these wires aside for later use.

# ASSEMBLY GUIDE

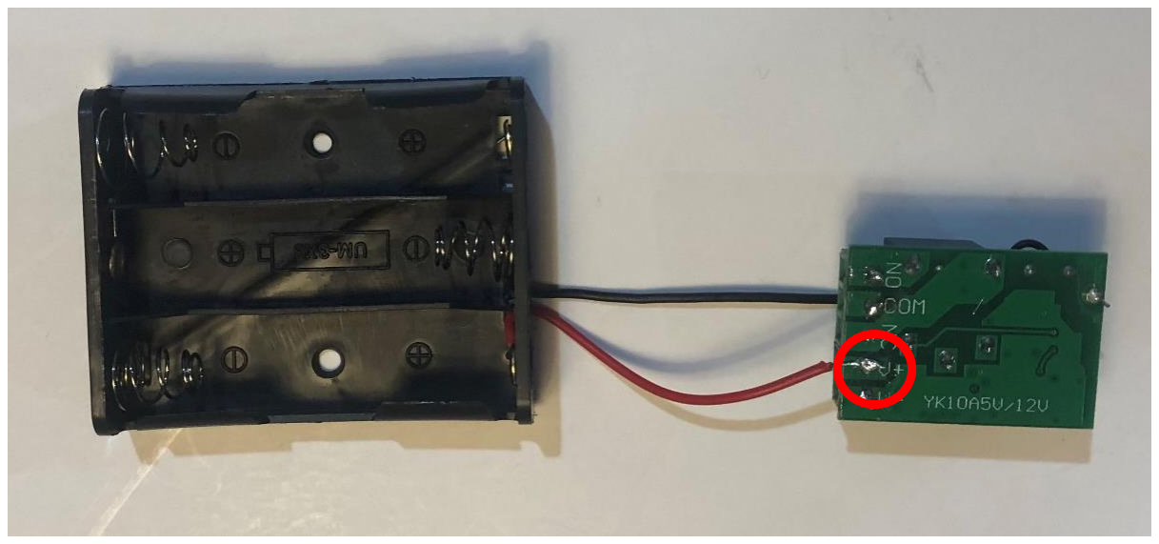
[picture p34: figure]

Files available at https://makersmakingchange.com/project/wireless-assistive-switch-link/ | Page 4 of 18
4.2.3 | Trim battery holder wires
Cut off approximately 8 cm from the red wire from the battery terminal. Strip off 0.5 cm to expose the wire.

## 4.2.4 Solder one battery holder lead to receiver PCB

Solder the other end of the red wire on the battery compartment to the V+ pin on the bottom of the receiver.

# ASSEMBLY GUIDE

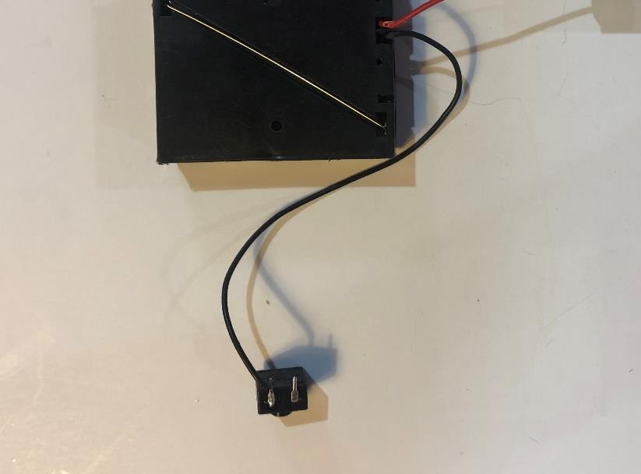
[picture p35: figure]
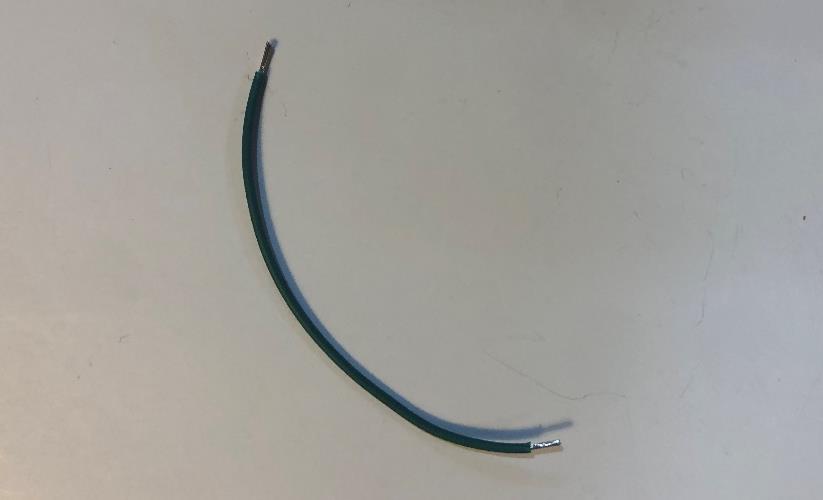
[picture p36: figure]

Files available at https://makersmakingchange.com/project/wireless-assistive-switch-link/ | Page 5 of 18
4.2.5 | Solder other battery holder lead to On/Off Switch
Solder the other end of black wire on the battery compartment to one leg of a latching switch.

## 4.2.6 Prep wire

Grab one of the 4 wires that were desoldered earlier from the receiver. Strip 0.5 cm from the end of each wire.

# ASSEMBLY GUIDE

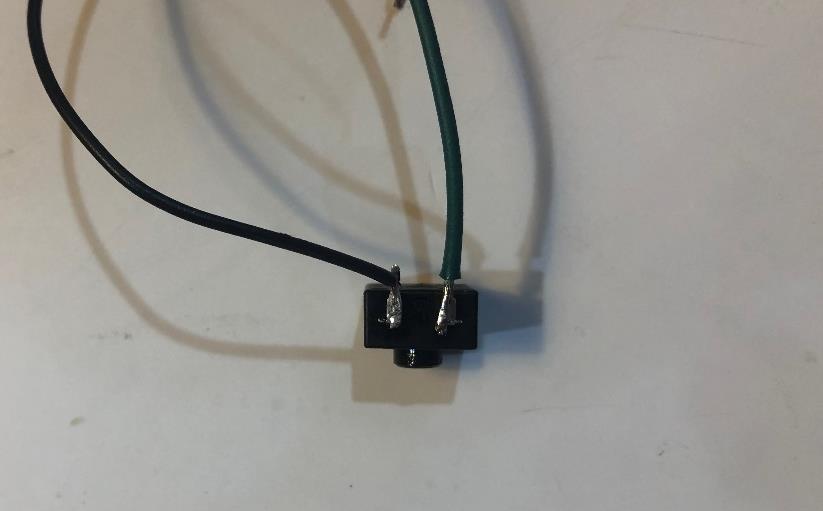
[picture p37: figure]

Files available at https://makersmakingchange.com/project/wireless-assistive-switch-link/ | Page 6 of 18
4.2.7 | Solder wire to On/Off Switch
Solder one end of the wire to the other leg of the same latching switch. This will be the On/Off switch for the device.

## 4.2.8 Solder Wire from On/Off Switch to Receiver PCB

Solder the other end of the wire to the V- pin on the bottom of the receiver.

# ASSEMBLY GUIDE

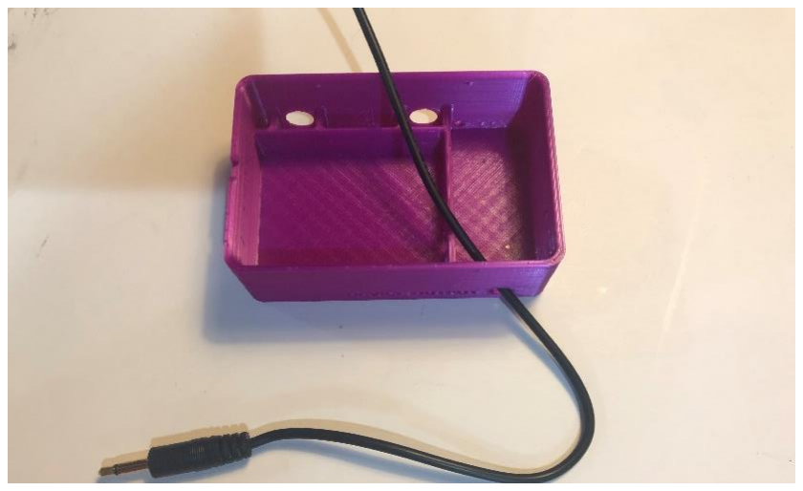
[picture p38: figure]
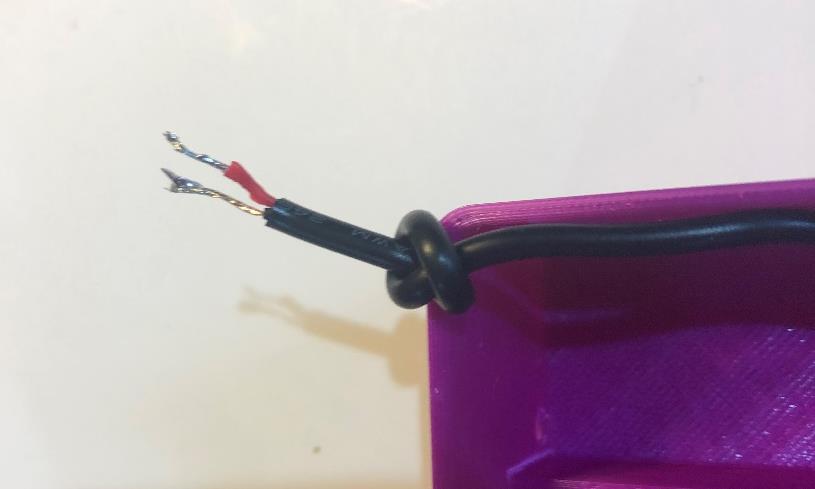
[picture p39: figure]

Files available at https://makersmakingchange.com/project/wireless-assistive-switch-link/ | Page 7 of 18
4.2.9 | Insert Cable into Receiver Enclosure
Thread the stripped ends of the male cable through the hole in the 3D print labeled Device Output.

## 4.2.10 Knot Cable

Tie a knot in the end of the wire approximately 2-3 from the ends of the stripped wires.

# ASSEMBLY GUIDE

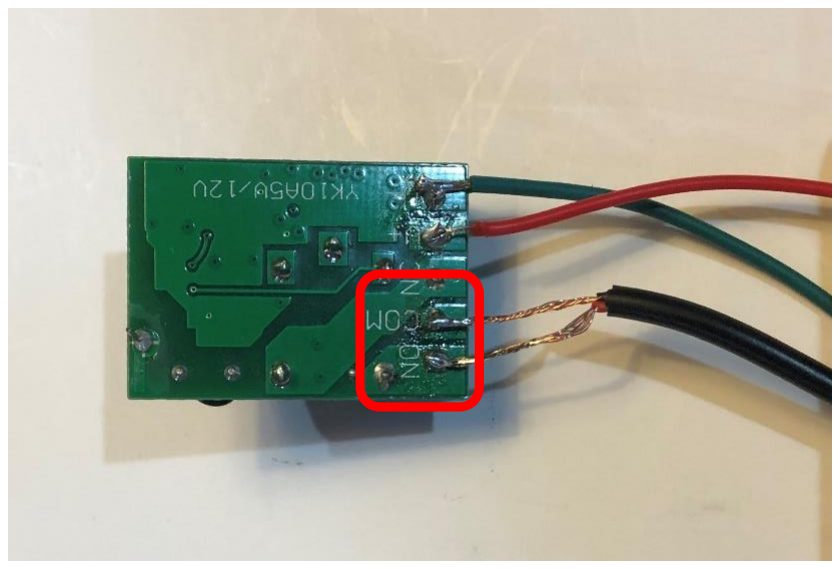
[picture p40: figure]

Files available at https://makersmakingchange.com/project/wireless-assistive-switch-link/ | Page 8 of 18

## 4.2.11 Solder 3.5 mm cable to Receiver PCB

Solder the two ends of the wire to the “NO” and “COM” pins on the bottom of the receiver.

## 4.2.12 Prep Mode Switch Wires

Grab 2 more of the wires you previously desoldered and set aside. Strip 0.5 cm from each end of the wire.

# ASSEMBLY GUIDE

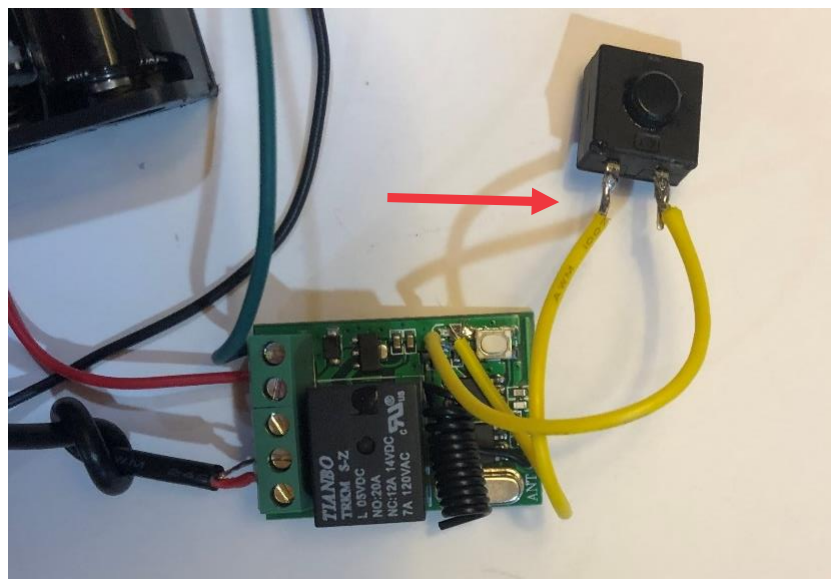
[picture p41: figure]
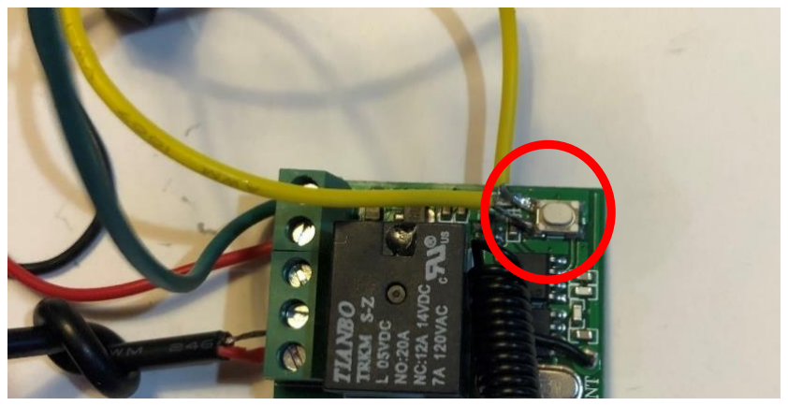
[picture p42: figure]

Files available at https://makersmakingchange.com/project/wireless-assistive-switch-link/ | Page 9 of 18

## 4.2.13 Solder Mode Switch Wires to Mode Switch

Solder one end of each of the wires to the legs on the second latching switch. This will be the mode button for the device.

## 4.2.14 Solder Mode Switch Wires to Receiver PCB

Solder the other two ends of the wires to the two legs of the switch located on the receiver as shown.

# ASSEMBLY GUIDE

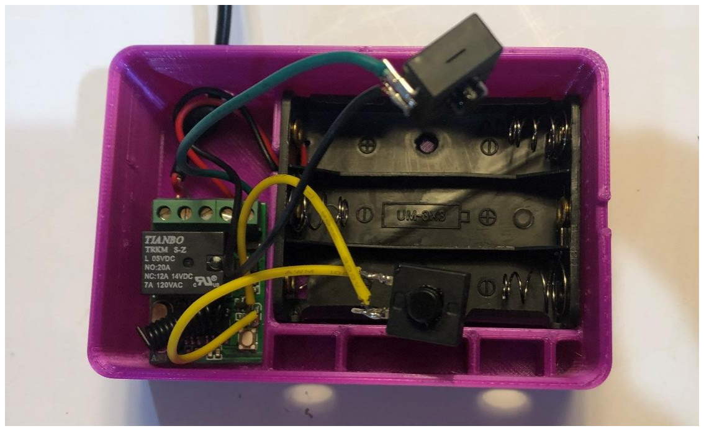
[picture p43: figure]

Files available at https://makersmakingchange.com/project/wireless-assistive-switch-link/ | Page 10 of 18

## 4.2.15 Insert Components into Receiver Enclosure

Place the battery compartment and the receiver in the 3D printed base as shown.

## 4.2.16 Insert On/Off Switch into Receiver Enclosure

Locate the switch soldered in Step 9 known as the On/Off Switch. While depressing the switch, slide it vertically down into the slot labelled “ON/OFF” on the print.

# ASSEMBLY GUIDE

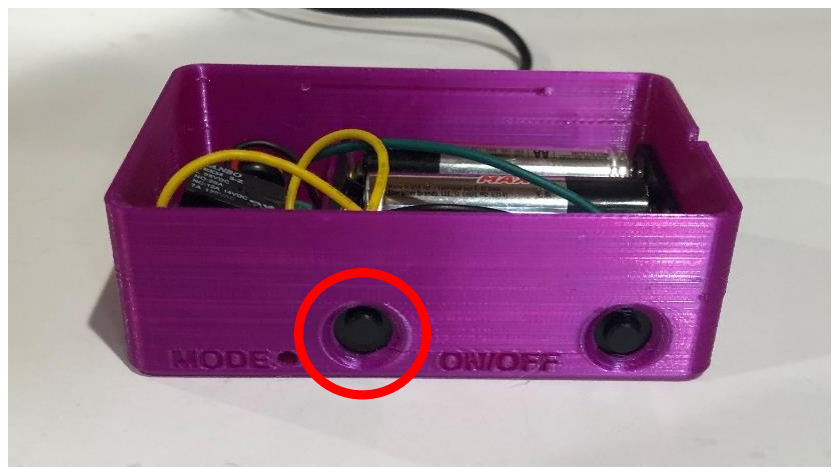
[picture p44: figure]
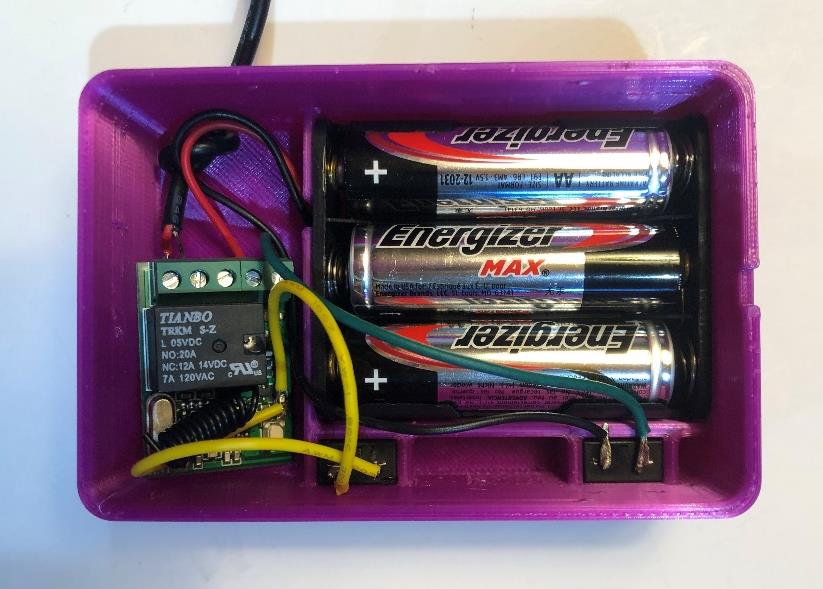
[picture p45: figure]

Files available at https://makersmakingchange.com/project/wireless-assistive-switch-link/ | Page 11 of 18

## 4.2.17 Insert Mode Switch into Receiver Enclosure

Do the same with the second latching switch. This time it will slide into the slot labelled

## “MODE”

## 4.2.18 Insert Batteries into Battery Holder

Insert 3 AA batteries into the battery holder. If the receiver starts blinking red, press the “MODE” button and it should turn off.

# ASSEMBLY GUIDE

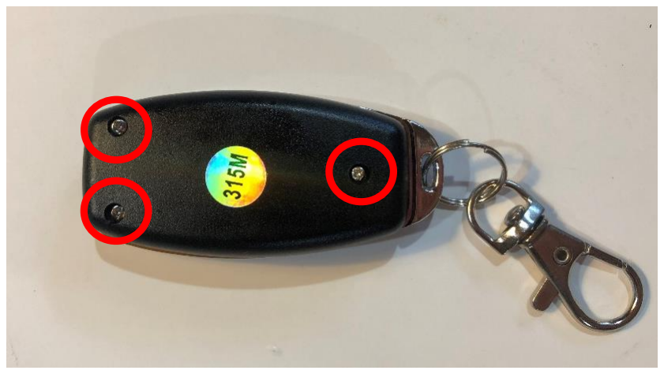
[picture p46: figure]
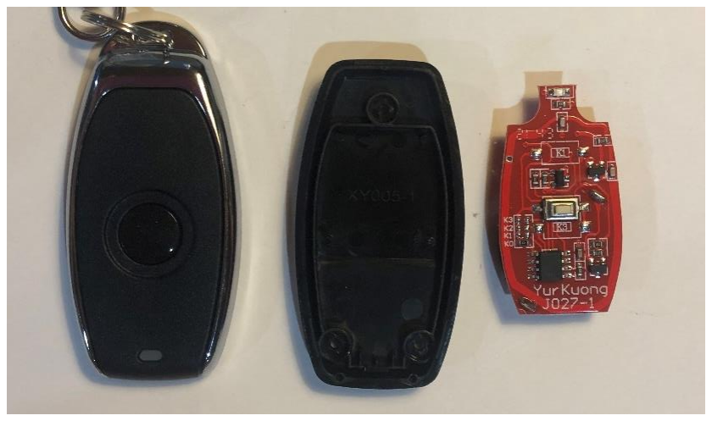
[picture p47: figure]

Files available at https://makersmakingchange.com/project/wireless-assistive-switch-link/ | Page 12 of 18

## 4.3 Transmitter

## 4.3.1 Open Transmitter Case

Remove the three screws from the back of the remote.

## 4.3.2 Disassemble Transmitter

Remove and set aside the remote casing.

# ASSEMBLY GUIDE


Files available at https://makersmakingchange.com/project/wireless-assistive-switch-link/ | Page 13 of 18
4.3.3 | Insert Cable into Transmitter Enclosure
With the female end of the 3.5 mm cable, thread the wire stripped end of the wire through the hole in the smaller 3D printed base labelled “Switch Input”.

## 4.3.4 Solder Cable to Transmitter PCB

Solder the two stripped wires to each side of the switch located in the middle of the board of the transmitter.

# ASSEMBLY GUIDE

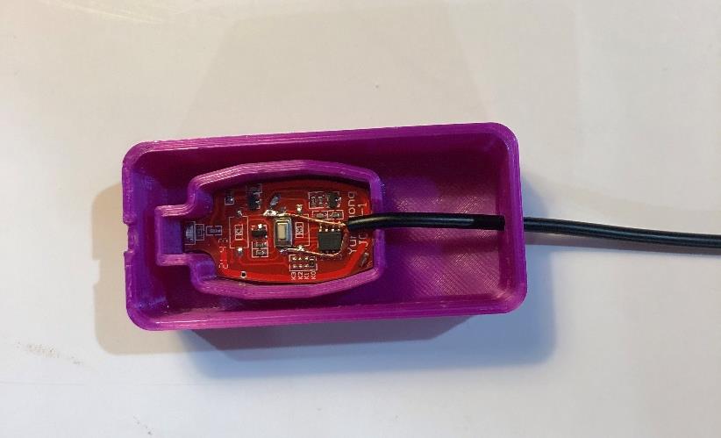
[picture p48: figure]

Files available at https://makersmakingchange.com/project/wireless-assistive-switch-link/ | Page 14 of 18
4.3.5 | Insert Transmitter PCB into Transmitter Enclosure
Place the transmitter in the 3D printed base as shown.

# ASSEMBLY GUIDE

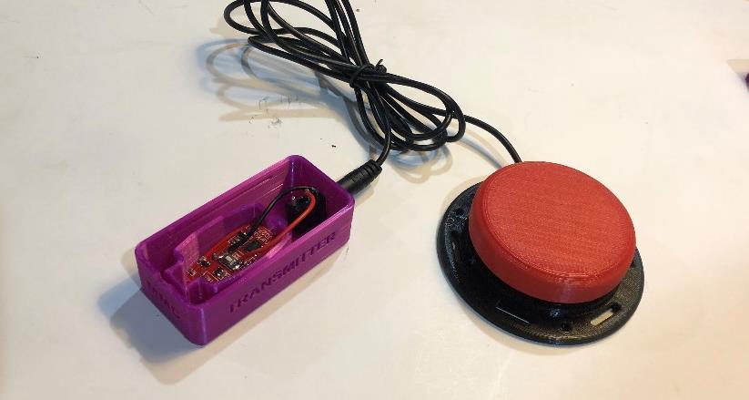
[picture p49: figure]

Files available at https://makersmakingchange.com/project/wireless-assistive-switch-link/ | Page 15 of 18

## 4.4 Testing

## 4.4.1 Attach Assistive Switch to Transmitter

Test the transmitter and receiver before putting on the enclosure covers. Plug a 3.5 mm switch into the female end of the 3.5 mm cable (on the transmitter).

## 4.4.2 Attach Receiver to Output Device

## From the receiver, connect the 3.5 mm male plug to the 3.5 mm connection on an output

device such as a switch adapted toy.

## 4.4.3 Test the Device

Activate the assistive switch. The toy should activate. If nothing happens, press the “ON/OFF” button on the receiver and try again. The toy might not activate yet but there will be a “clicking

## sound and a red-light flash

# ASSEMBLY GUIDE

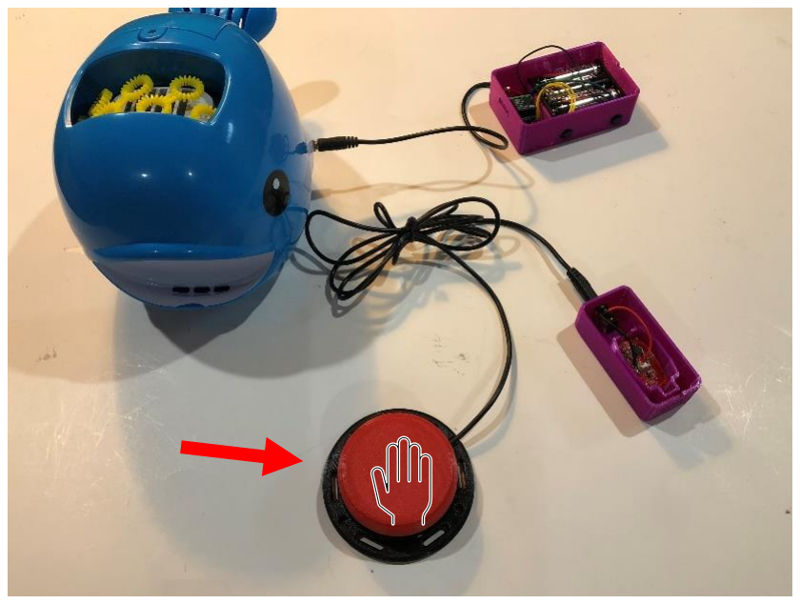
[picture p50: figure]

Files available at https://makersmakingchange.com/project/wireless-assistive-switch-link/ | Page 16 of 18

# ASSEMBLY GUIDE

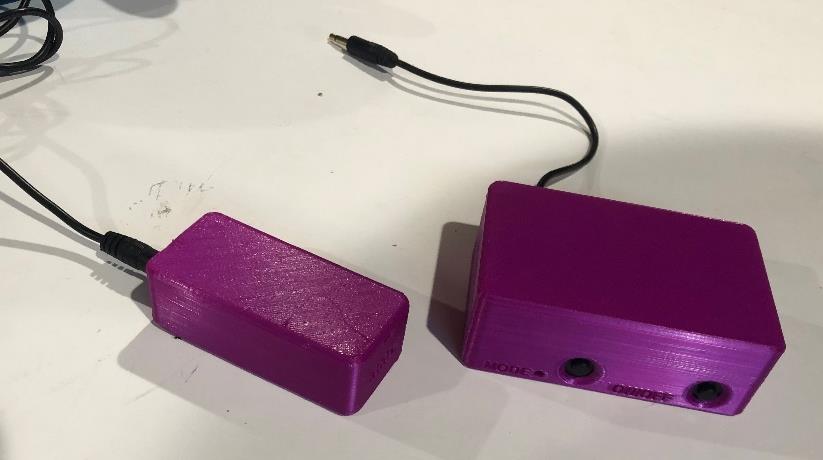
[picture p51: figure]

Files available at https://makersmakingchange.com/project/wireless-assistive-switch-link/ | Page 17 of 18

## 4.5 Final Assembly

## 4.5.1 Add Covers to Enclosures

Once the devices are working, add the cover to each enclosure by snapping them in to place.

# ASSEMBLY GUIDE

Files available at https://makersmakingchange.com/project/wireless-assistive-switch-link/ | Page 18 of 18

## 4.6 Setting Activation Mode

## 4.6.1 Change Activation Mode

There are several different modes offered on the receiver. If you press the “MODE” button, the device should start to flash. It will do one flash, pause, two flashes, pause, 3 flashes, pause, all the way up to 7 flashes. To select a mode, press the “MODE” button again after you see the

## number of flashes for the setting you want. For example, if you want to use to momentary

switch function, press the mode button, then wait for the red light to flash twice in a row, then

## press the mode button again. The following is a guide to explain the different modes:

## 1 flash = What seems to be an infinite latch? It does not appear to be useful and would

recommend not using it.

2 flashes = momentary switch. The output device will turn off about 0.5 seconds after the user stops pressing the switch.

3 flashes = latching switch. It will stay on until you press the assistive switch again to turn it off.

4 flashes = switch latches for 10 seconds and then turns off.

5 flashes = switch latches for 1 minute and then turns off.

6 flashes = switch latches for 5 minutes and then turns off.

7 flashes = An “error”. Avoid using this setting. If you accidentally set the device to the 7th setting, it will not do anything. The device will have to be resynced by pressing the mode button twice quickly until the red light stays on. Next, click the assistive switch. Then, press the mode button again to pick the mode you want. The device should work again once this is complete.

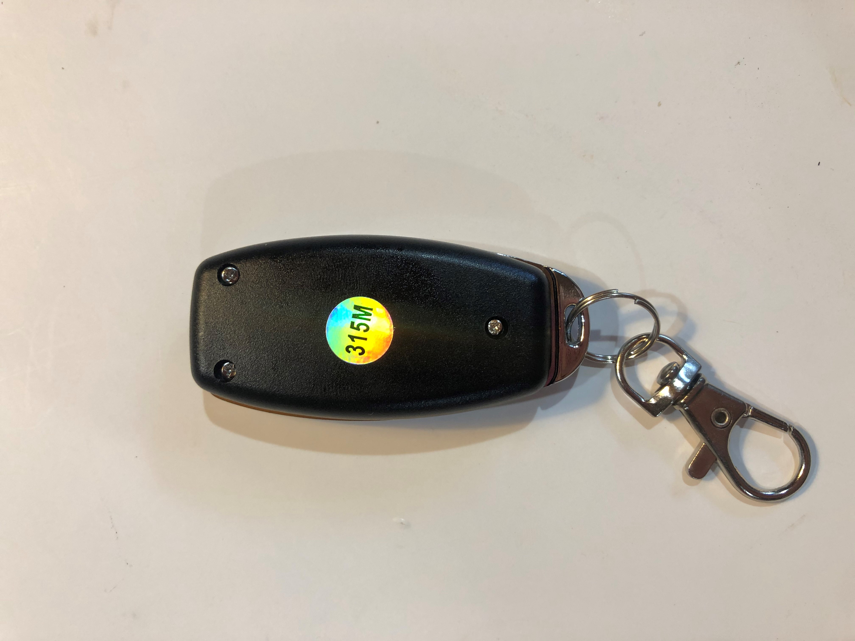
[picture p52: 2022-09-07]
Documentation/Working_Documents/Assembly_Photos/Step 1.jpg

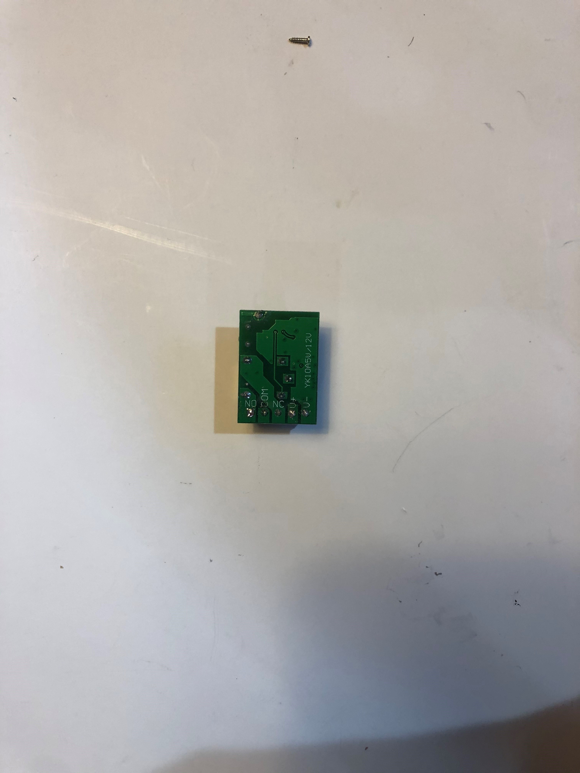
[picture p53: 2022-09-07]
Documentation/Working_Documents/Assembly_Photos/Step 4B.jpg

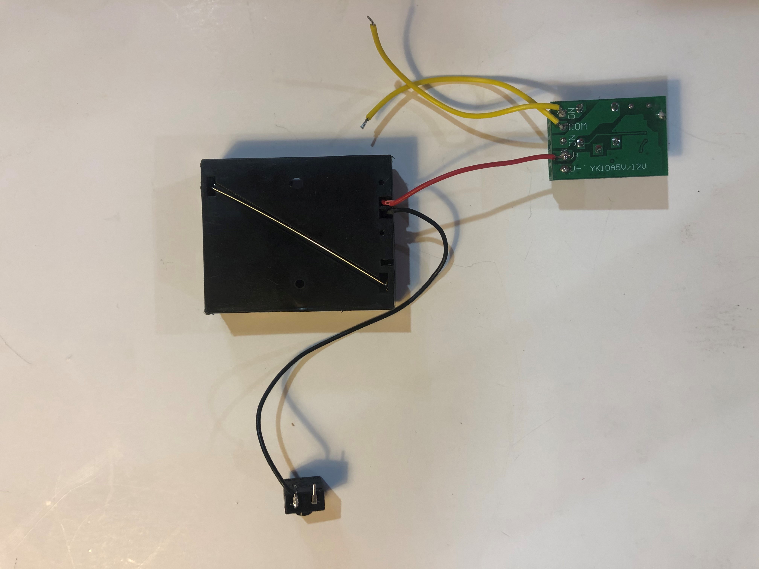
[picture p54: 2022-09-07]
Documentation/Working_Documents/Assembly_Photos/Step 7.jpg

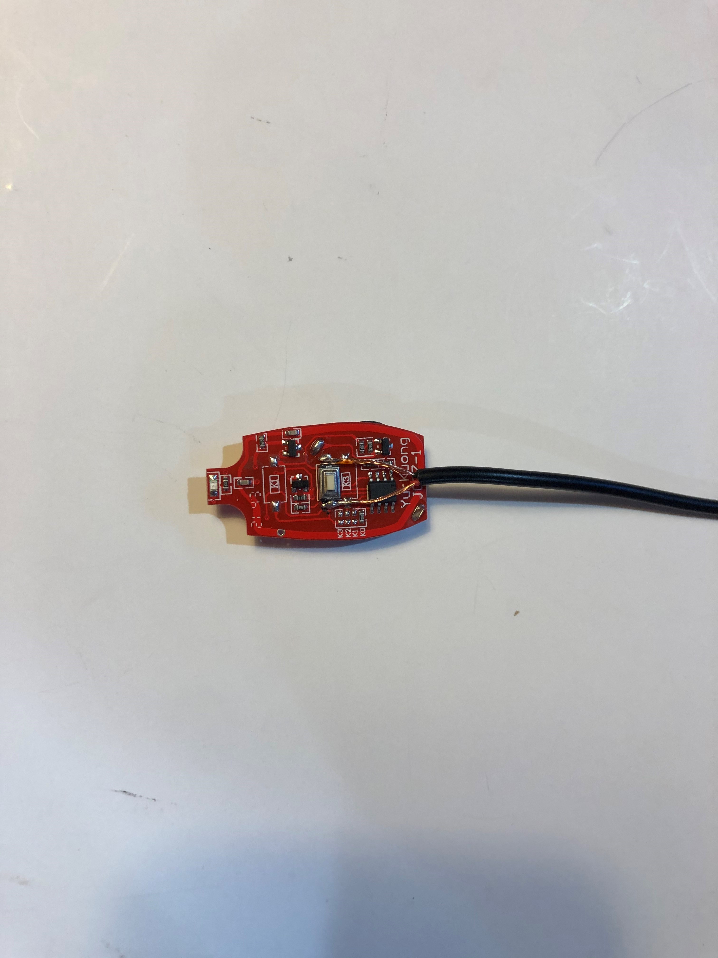
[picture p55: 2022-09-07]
Documentation/Working_Documents/Assembly_Photos/Step 24.jpg

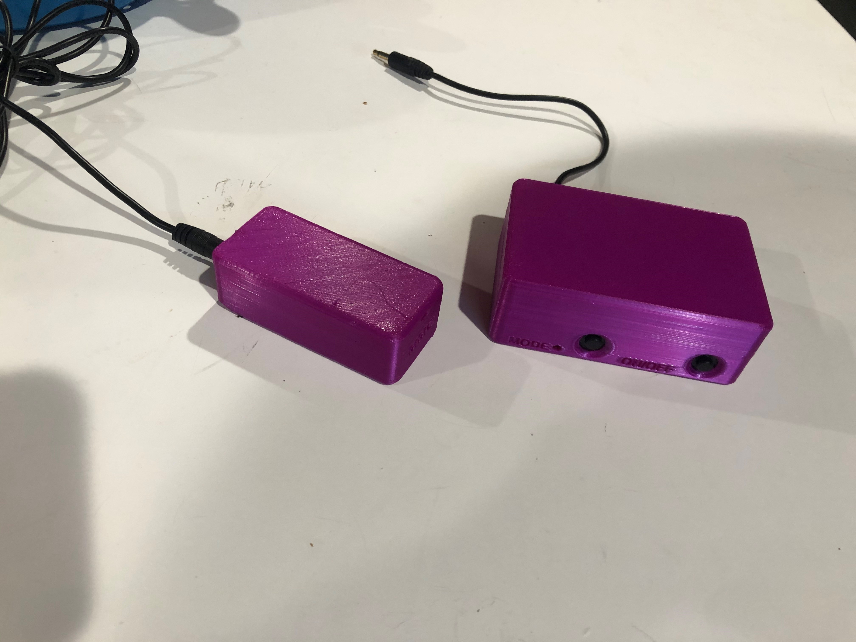
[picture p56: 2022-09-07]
Documentation/Working_Documents/Assembly_Photos/Step 30.jpg

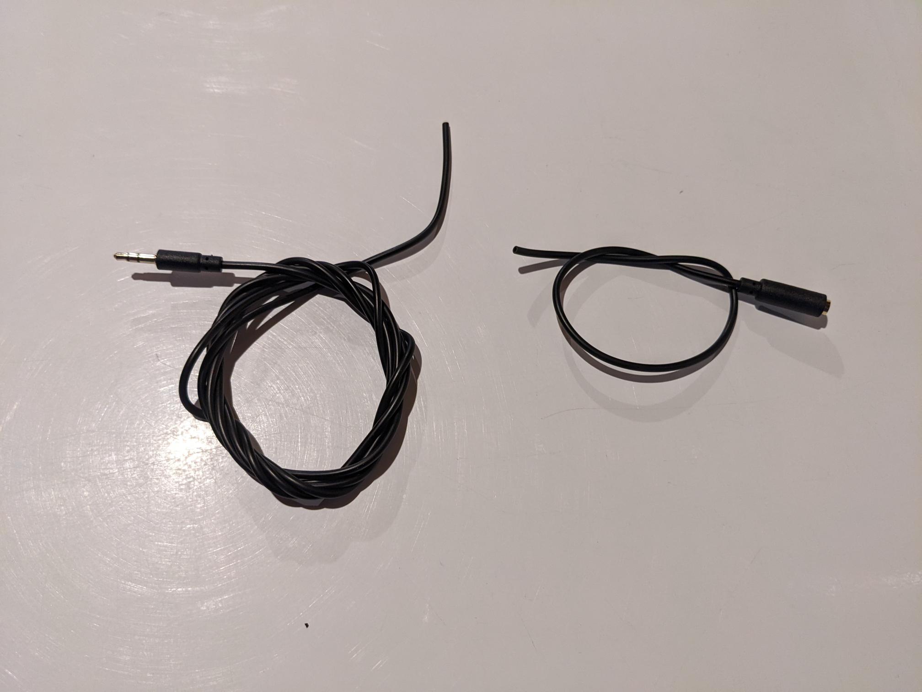
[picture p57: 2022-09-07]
Documentation/Working_Documents/Assembly_Photos/Step 11.png

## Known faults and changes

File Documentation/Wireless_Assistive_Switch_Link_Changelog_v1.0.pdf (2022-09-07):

V1.0 | AUGUST 2022

# Wireless Assistive Switch Link

# CHANGELOG

© 2022 by Neil Squire / Makers Making Change. This work is licensed under the CC BY SA 4.0 License: http://creativecommons.org/licenses/by-sa/4.0
Files available at https://makersmakingchange.com/project/wireless-assistive-switch-link/ | Page 1 of 1

# Version 1.0 | 2022-Aug-08

## - Initial Version - Designed by Kerilyn Kennedy – Makers Making Change - Documentation by Neil Squire / Makers Making Change
